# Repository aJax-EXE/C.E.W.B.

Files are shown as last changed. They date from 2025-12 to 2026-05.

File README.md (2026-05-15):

# C.E.W.B.: The Open Source Teaching Platform for Control Systems
**ECEN4620/MCEN4085: Senior Design Project - University of Colorado Boulder**  
**Sponsors:** Talles Santos  
&emsp;&emsp;&emsp;&emsp;&emsp; Nathan McNeil  
**Students:** [Alyssa Jackson](https://github.com/aJax-EXE) (Electrical and Computer Engineering)  
&emsp;&emsp;&emsp;&emsp;&emsp;Eric Pollert (Mechanical Engineering)  
&emsp;&emsp;&emsp;&emsp;&emsp;[Isaiah Knox](https://github.com/iknox001) (Mechanical Engineering)  

---

## Table of Contents
1. [Introduction](#introduction)
2. [Project Overview](#project-overview)
3. [System Specifications](#system-specifications)
4. [Repository Structure](#repository-structure)
5. [Hardware](#hardware)
   - [Circuit Design](#circuit-design)
   - [Data Transmission](#data-transmission)
   - [Accessory Storage](#accessory-storage)
   - [Device Deck](#device-deck)
   - [Motor Housing](#motor-housing)
   - [Electrical Compartment](#electrical-compartment)
   - [Attachments](#attachments)
6. [Software](#software)
   - [Dependencies](#dependencies)
   - [Arduino Code](#arduino-code)
   - [MATLAB/Simulink Interface](#matlabsimulink-interface)
   - [Custom Libraries](#custom-libraries)
7. [Getting Started](#getting-started)
   - [Hardware Setup](#hardware-setup)
   - [Software Setup](#software-setup)
   - [Running Your First Experiment](#running-your-first-experiment)
8. [Lab Experiments](#lab-experiments)
   - [Angular Position Control (Inertia Disc)](#angular-position-control-inertia-disc)
   - [Inverted Pendulum Balancing](#inverted-pendulum-balancing)
9. [Results](#results)
10. [Known Limitations](#known-limitations)
11. [Next Steps](#next-steps)
    - [List of Issues](#list-of-issues)
    - [After CEWB Functionality is Reached](#after-cewb-functionality-is-reached)
12. [Contributing](#contributing)
13. [License](#license)

---

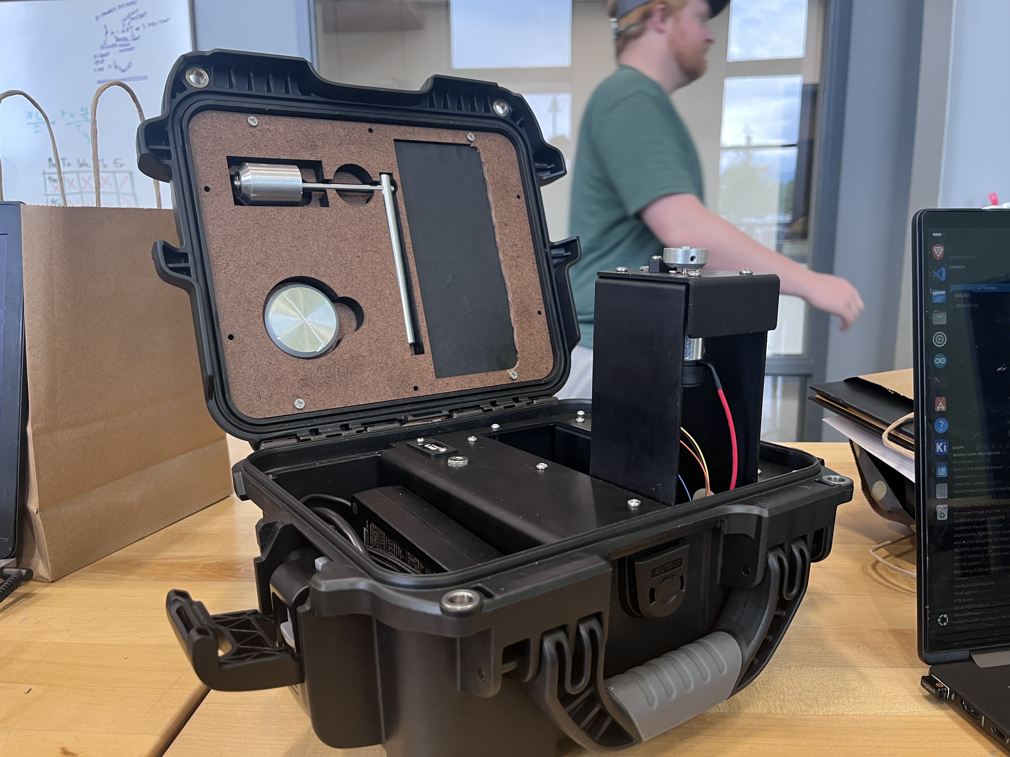
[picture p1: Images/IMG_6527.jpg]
The CEWB
  
*The CEWB, fully built*  
&emsp;

---

## Introduction

C.E.W.B. (name pending; referred to as 'CEWB' throughout this README) is a low-cost, open-source electromechanical teaching platform designed for teaching and applying control systems concepts in a real-world environment. It was developed as a direct functional replacement for the Quanser Qube-Servo 2, a $5,000 proprietary device that is now outdated and requires an older version of MATLAB to operate.

The device supports the same core laboratory experiments as the Qube-Servo 2, including angular position control with an inertia disc and inverted pendulum balancing. It is designed to be self-contained, portable, and fully compatible with MATLAB and Simulink.

All design files, code, and documentation are publicly available in this repository so that the device can be reproduced by any institution without reliance on proprietary hardware or software.

---

## Project Overview

This project set out to design a low-cost, open-source replacement for the Quanser Qube-Servo 2, a $5,000 device used in control systems classes. The target was a fully functional prototype delivered by May 2026 at under $1,000 per unit, capable of supporting the same lab experiments — including angular position control with an inertia disc and inverted pendulum balancing — while being self-contained, portable, and compatible with MATLAB/Simulink.

The design integrates all components into a Nanuk 905 protective case with built-in storage for attachments, cables, and the power supply. The system uses an Arduino microcontroller, a motor driver, and a custom PCB, with two interchangeable magnetic attachments — an inertia disc and a pendulum — mirroring the Qube-Servo 2's functionality. The projected per-unit production cost of $763.68 comes in well under the $1,000 target.

The device met most implementation requirements. Data transmission, MATLAB/Simulink compatibility, third-party manufacturability, self-contained storage, and transport protection all passed evaluation. Open-source documentation, including CAD files, a bill of materials, and assembly instructions, has been prepared and made publicly available.

However, the device did not fully replicate the closed-loop control performance of the Qube-Servo 2. The Arduino's data transmission rate is approximately an order of magnitude slower than the proprietary controller used in the Qube-Servo 2, causing significant control loop delays and excessive overshoot during inertia disc testing. As a result, the pendulum balancing test was not attempted.

The primary recommended next step is to replace the Arduino with a faster microcontroller, retest the system using the same control experiments, and proceed to a small production run once performance requirements are confirmed to be met.

---

## System Specifications

The following table lists the key performance parameters of the C.E.W.B. system alongside the Qube-Servo 2 equivalents for reference.

| Parameter | C.E.W.B. | Qube-Servo 2 |
|---|---|---|
| Motor | Maxon DC-max 26 S Ø26 mm | Maxon (discontinued) |
| Nominal input voltage | 24 V | 18 V |
| Nominal torque | 22.0 mN-m | 22.0 mN-m |
| Nominal speed | 3050 RPM | 3050 RPM |
| Encoder line count | 512 lines/rev | 512 lines/rev |
| Encoder resolution (quadrature) | 2048 counts/rev | 2048 counts/rev |
| Encoder resolution (deg) | 0.176 deg/count | 0.176 deg/count |
| Encoder resolution (rad) | 0.00307 rad/count | 0.00307 rad/count |
| Motor controller | Adafruit DRV8871 | PWM amplifier |
| Microcontroller | Arduino Uno R3 | Proprietary |
| Data transmission rate | ~50 Hz (USB serial) | ~500 Hz (proprietary) |
| Output voltage range | ±24 V | ±10 V (recommended) |
| Per-unit cost (production) | $763.68 | $5,000.00 |

---

## Repository Structure

```
C.E.W.B./
├── Datasheets/
│   ├── Electrical/                                # Datasheets for all electrical components
│   └── Hardware/                                  # Datasheets for hardware components
├── Documentation/                                # Documentation from the Senior Projects Class
├── Hardware/
│   ├── 3DModels/
│   │   ├── CurrentVersion/                       # Final production CAD files (SolidWorks)
│   │   │   ├── Device Components/                # All structural device parts
│   │   │   │   ├── Full Assembly.SLDASM
│   │   │   │   ├── Motor Arm.SLDASM
│   │   │   │   ├── Housing.SLDPRT
│   │   │   │   ├── Motor Plate.SLDPRT
│   │   │   │   ├── Motor Leg.SLDPRT
│   │   │   │   ├── Plate bend inlet.SLDPRT
│   │   │   │   ├── Inertia Disc.SLDPRT
│   │   │   │   ├── Attachment Interface.SLDPRT
│   │   │   │   ├── Pendulum Assembly.SLDASM
│   │   │   │   ├── Pendulum mount.SLDPRT
│   │   │   │   ├── Pendulum shaft.SLDPRT
│   │   │   │   ├── Pendulum Arm.SLDPRT
│   │   │   │   ├── Pendulum Stop.SLDPRT
│   │   │   │   ├── PCB.SLDPRT
│   │   │   │   ├── PCB Mounting Plate.SLDPRT
│   │   │   │   └── [purchased hardware SLDPRTs]
│   │   │   └── Storage Compartment Components/   # Lid storage assembly parts
│   │   │       ├── Foam_Panel.SLDPRT
│   │   │       ├── Front Panel.SLDPRT
│   │   │       └── Rear Lid Panel.SLDPRT
│   │   └── PastVersions/                         # Design iteration history
│   └── PCBModels/
│       ├── ArduinoShieldDesign/                  # KiCad PCB design files
│       │   ├── ForwardDesign/                    # Current production PCB
│       │   ├── ReverseDesign/                    # Earlier PCB iteration
│       │   ├── OldTestBoard/                     # First test board
│       │   └── PotentialFix/                     # Proposed PCB fix iteration
│       ├── GerberFiles/
│       │   ├── ForwardFiles/                     # Gerber files for production PCB
│           └── ReverseFiles/                     # Gerber files for reverse design
├── Images/                                       # Images used in this README and in the documentation
├── Software/
│   ├── Libraries/                                # Arduino libraries — install these manually
│   │   ├── CombiningEncoderCounts/               # CEWBEncoder source
│   │   │   ├── CEWBEncoder.cpp
│   │   │   └── CEWBEncoder.h
│   │   └── OtherFunctions/                       # CEWBFunctions source
│   │       ├── CEWBFunctions.cpp
│   │       └── CEWBFunctions.h
│   ├── ExamplesAndTests/
│   │   ├── ArduinoTests/                         # Standalone Arduino diagnostic sketches
│   │   │   ├── CalcToAnalogVal/                  # PWM value calculator
│   │   │   ├── CommunicationConstantlySendingData/  # Serial format test
│   │   │   ├── EncoderQuadTest/                  # Encoder wiring verification
│   │   │   ├── InterruptEncoderTest/             # Interrupt-based encoder test
│   │   │   └── MotorRampSpeedTest/               # Motor driver verification
│   │   ├── ProofOfConcept/                       # Early proof-of-concept scripts
│   │   └── SimulinkTests/                        # Simulink integration test models
│   │       ├── BasicSimulinkCommunication/       # Initial serial block example
│   │       ├── BypassSerialBlockSimulinkConnectionTest/
│   │       ├── CompleteSimulinkRunTest/
│   │       │   ├── BasicRunning/                 # Open-loop voltage test model
│   │       │   └── WorkingModel/                 # ⭐ Main working model
│   │       │       ├── ArduinoSerial.m           # MATLAB System block
│   │       │       ├── WorkingModel.ino          # Arduino sketch
│   │       │       └── PIDController.slx         # Simulink model
│   │       ├── SimulinkFormattingTest/
│   │       └── SimulinkReadEncoder/              # Encoder-only read test
│   ├── SendingBytesTest/                         # Binary byte transmission experiment
│   ├── SimulinkReadWriteSerialPort/              # Early serial block experiments
│   ├── SpinMotorWithSimulinkTest/                # Motor spin test
│   └── UpgradedMotorWSimulinkTest/               # Updated motor test
├── .gitignore
└── README.md
```
 
> ⭐ **For most users, the only files needed are in `Software/ExamplesAndTests/SimulinkTests/CompleteSimulinkRunTest/WorkingModel/`** — the Arduino sketch, MATLAB System block, and Simulink model are all there.
---

## Hardware

&emsp;
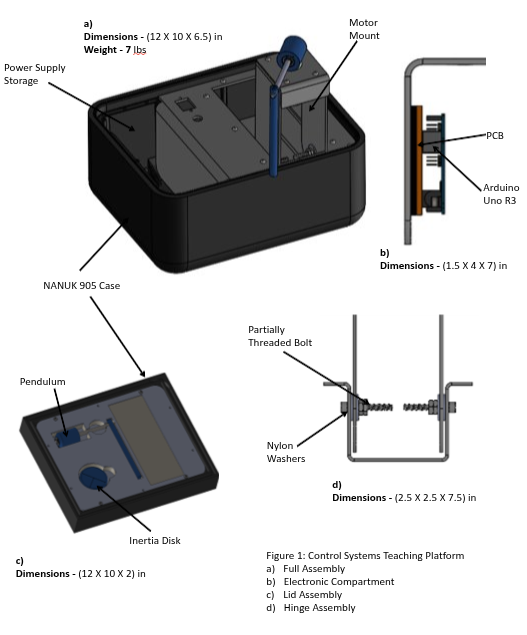
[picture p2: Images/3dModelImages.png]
3D Models of the CEWB
  
*3D models of the CEWB and its parts*  
&emsp;

### Circuit Design

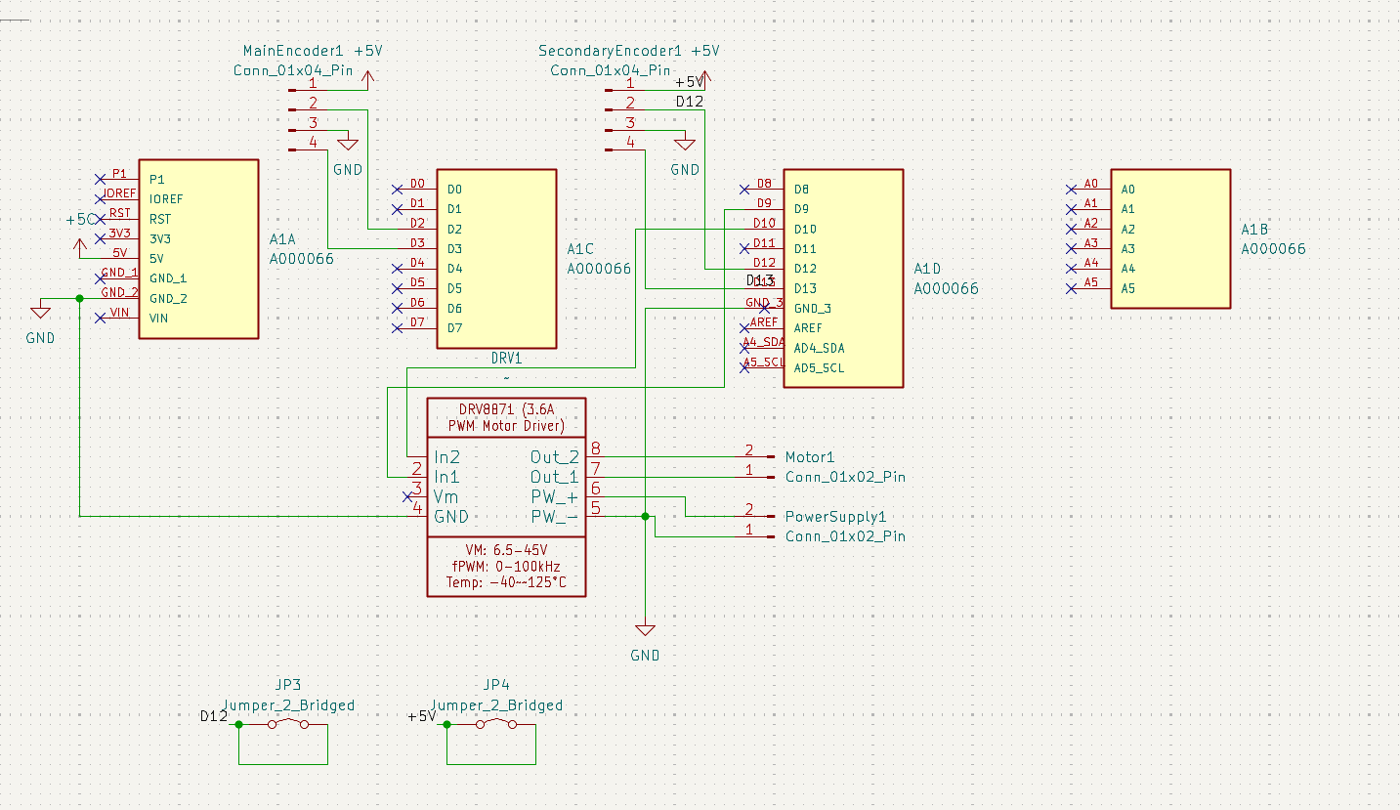
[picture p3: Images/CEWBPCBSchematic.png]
The CEWB Schematics
  
*The CEWB electrical schematic*  
&emsp;

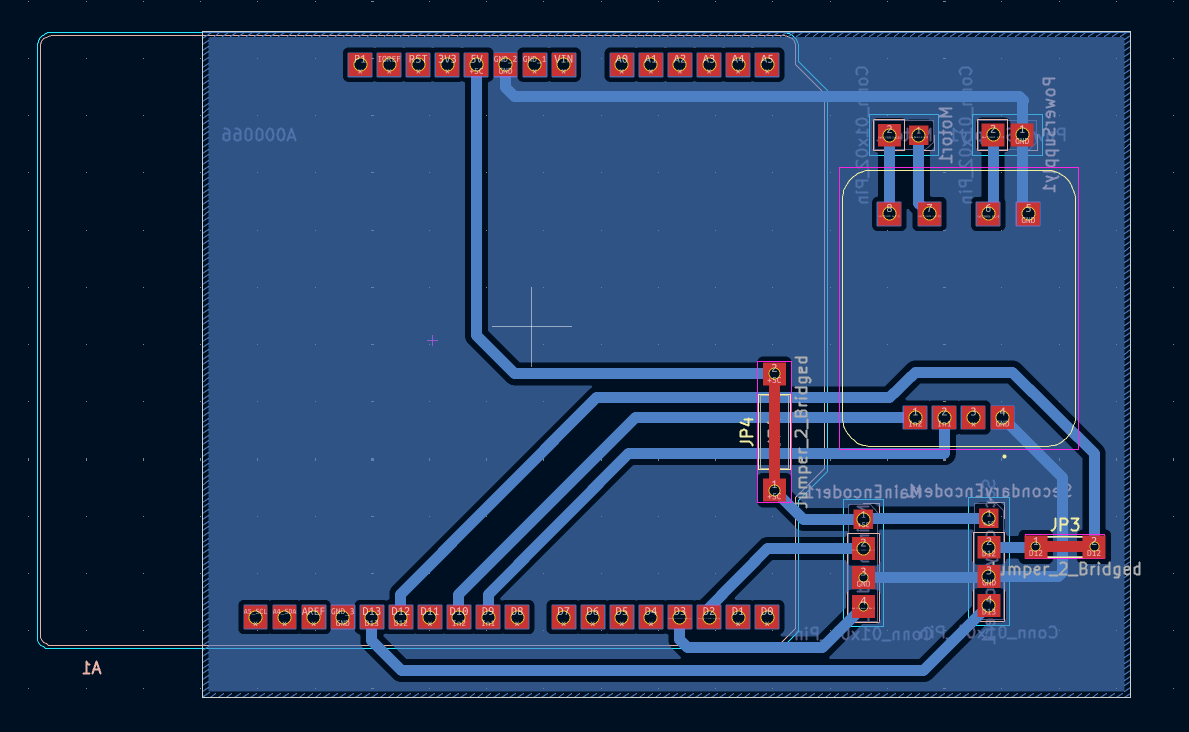
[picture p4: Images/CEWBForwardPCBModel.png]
The CEWB PCB Model
  
*The CEWB PCB model*  
&emsp;

The electrical system is built around an Arduino Uno R3 microcontroller and an Adafruit DRV8871 motor driver, both connected through a custom PCB. The PCB acts as a junction point between the motor, encoders, and microcontroller, consolidating all wiring and reducing the risk of loose connections. A 24V Mean Well GST90A24-P1M power supply provides power to the system via a front-panel power port. A front-panel USB-B port connects the Arduino to the user's laptop for data transmission.

The PCB is insulated from the aluminum mounting panel using an acrylic backing plate to prevent electrical interference.

### Data Transmission

Communication between the Arduino and MATLAB/Simulink is handled over USB serial at 115200 baud using a custom request/response packet protocol. Simulink sends a scaled integer voltage command, and the Arduino responds with the current encoder count and applied voltage. The full protocol is described in the [Arduino Code](#arduino-code) section of the Software documentation.

### Accessory Storage

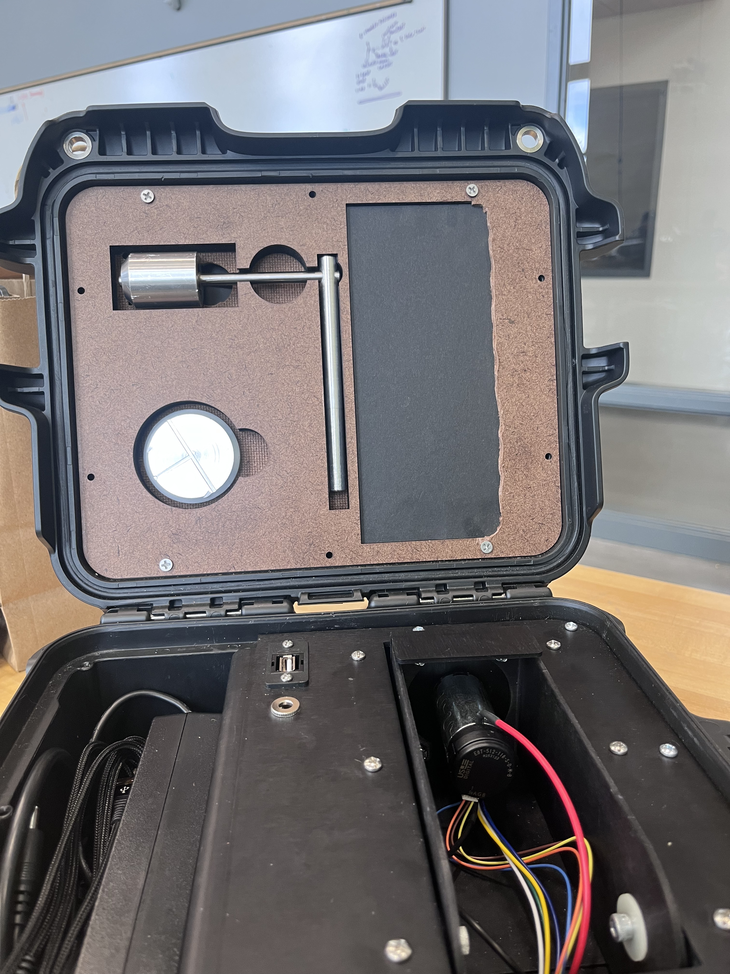
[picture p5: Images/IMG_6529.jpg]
The Storage Lid
  
*The storage lid that houses the CEWB attachments*  
&emsp;

The accessory storage compartment is made up of two pieces of hardboard and one piece of foam with cutouts for the accessories to fit into. The rear panel of hardboard has magnets glued into it, which allow the attachments to be secured in their respective locations during storage. Hardboard was selected for the front and rear panels as it is a light, cheap, and sturdy material. Foam was chosen for the middle panel as it is low-density and fills the space between the boards without significantly increasing weight. The three panels are glued together with super glue and are fixed into the top of the Nanuk 905 case using thread-forming screws.

### Device Deck

The main part of the deck of the device is a bent piece of aluminum sheet metal which is screwed into the Nanuk 905 case using thread-forming screws and serves as a mounting plate for the rest of the components. This part is bent to create a compartment for storing the power supply and the data transmission cable. The top surface of this panel has two ports: a USB port where the data transmission cable is plugged in, and a power port where the device is connected to the power supply. The ports were added to clean up the visual appearance of the device and remove the need for cables to be plugged directly into the electrical compartment. On the right side of the panel there is a cavity with a U-shaped bent piece of aluminum sheet metal mounted to the bottom of the panel, which serves both as a mounting location for the motor housing and as a barrier between the user and the internal components. The cavity allows the motor housing to fold into the device when stored. The trough contains a hole to allow wires to pass through between the motor housing and the electrical compartment. This hole is lined with a silicone grommet which protects the wires from fraying when the motor housing is moved between its storage and operating positions.

### Motor Housing

The motor housing consists of three main structural components, all made from aluminum sheet metal. The two motor housing legs give the housing the height required for the pendulum attachment and serve as the mounting location for the hinge, which allows the housing to pivot between its operational and storage positions. The hinge consists of a partially threaded socket head screw, nuts, and nylon washers. The partially threaded screw was chosen to provide a smooth surface for the hinge to rotate on. The nylon washers secure the housing in place during operation while still allowing rotation under sufficient force to slightly deform the nylon. The two washers at the end are jammed together to secure the hinge at a calibrated tightness, ensuring the hinge can be rotated but remains secured during operation.

The third structural component is the motor mounting plate, which features a bend that serves as a handle when switching the device between positions. This plate is attached at the top of the two motor legs using bolts and locknuts, and has the motor mounted to its underside using machine screws secured directly into threaded holes in the top of the motor. The motor is from Maxon and was chosen to replicate the motor of the Qube-Servo 2 as closely as possible given that the original motor is no longer available. An optical encoder is mounted to the rear axle of the motor using double-sided adhesive, which allows the encoder to be secured firmly without screws, as there are no mounting locations on the rear of the motor. The attachment interface is a small machined aluminum disc mounted to the end of the top motor shaft using a set screw. This component has magnets that allow the attachments to be fixed to the motor shaft during use. The motor plate also has a small 3D-printed elbow-shaped component mounted near the motor, which serves as a stop to prevent the pendulum from over-rotating and damaging its wiring. The mounting plate also has a 3.5 mm jack port for connecting the encoder from the pendulum attachment during use.

### Electrical Compartment

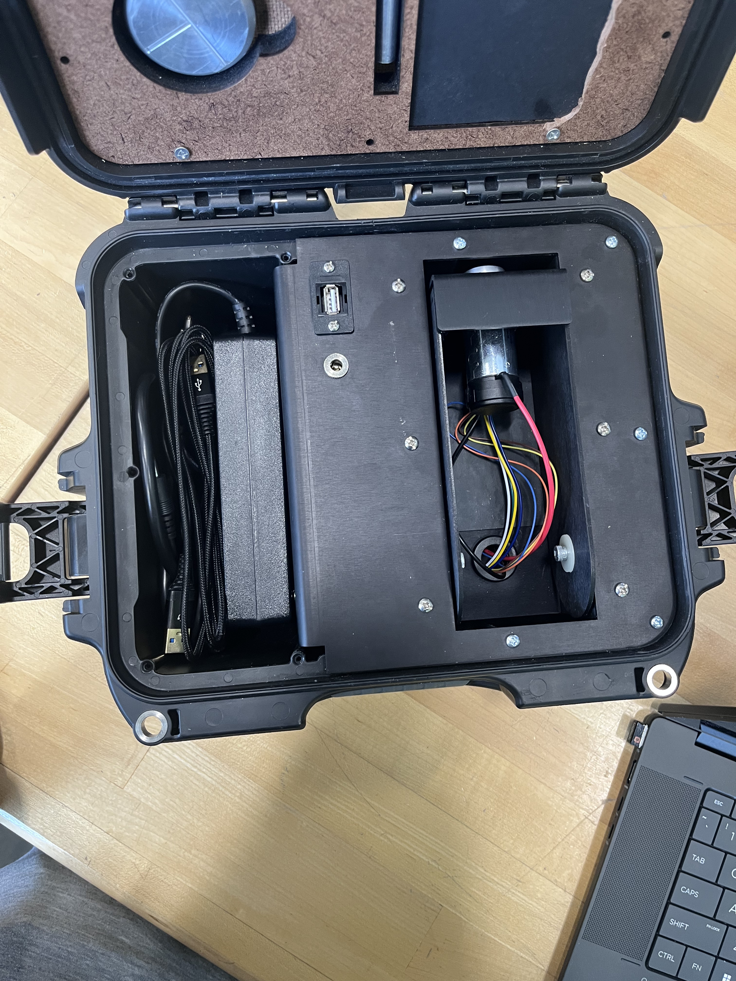
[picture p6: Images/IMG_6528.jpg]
The CEWB electrical compartment
  
*The CEWB electrical compartment*  
&emsp;

The electrical compartment is located between the bend in the top panel of the device deck and the trough. The electrical components — including the motor driver, Arduino, and PCB — are mounted to the backside of the panel using nuts and bolts, with a piece of acrylic sized to match the PCB placed behind it to insulate the exposed circuitry from the aluminum panel and prevent electrical interference.

### Attachments

The two attachments are the inertia disc and the pendulum. The inertia disc is a machined aluminum disc which adds rotational inertia to the motor shaft for use in position control experiments. The disc has lines engraved into its top surface which allow the user to visually track the motor's position and verify control system behavior. The disc has four magnets on the back which allow it to be secured to the attachment interface during use and to the attachment storage compartment when stored.

The pendulum consists of three machined components. The pendulum cylinder is machined from aluminum and is the mounting location for the pendulum assembly. It has magnets on one side for mounting to the attachment interface and storage compartment, and two bearings press-fit into its internal bore which allow the pendulum axle to rotate freely. The pendulum axle is made from steel and is inserted through the two bearings and secured using two retaining rings that fit into grooves in the axle positioned to press against the bearings. An optical encoder is attached to the pendulum cylinder using machine screws and tracks the angular position of the axle during pendulum experiments. The encoder connects via a 3.5 mm cable to a jack on the motor mounting plate, allowing encoder data to be transmitted to the electrical compartment. The pendulum arm is mounted on the far end of the axle using a set screw and acts as a counterweight to create the tipping moment that the control system must compensate for in the inverted pendulum experiment.

---

## Software

### Dependencies

**Arduino IDE (1.8.x recommended)**
- CEWBEncoder (included in `Software/MATLAB/Libraries/CEWBEncoder/`)
- CEWBFunctions (included in `Software/MATLAB/Libraries/CEWBFunctions/`)

**MATLAB/Simulink**
- MATLAB R2024b or later
- Simulink
- No additional toolboxes required — serial communication is handled via a custom `matlab.System` object

### Arduino Code

The main Arduino sketch (`WorkingModel.ino`) implements a simple request/response serial protocol. Simulink sends a voltage command, the Arduino executes it on the motor, and responds with the current encoder count and applied voltage.

**Packet format:**

| Direction | Format | Example |
|---|---|---|
| Simulink → Arduino | `#sXXXXXX\n` | `#+037500\n` (3.75V × 10000) |
| Arduino → Simulink | `#sXXXXXX,sXXXXXX\n` | `#+000512,+037500\n` |

Voltage is transmitted as a scaled integer (real volts × 10000) to preserve 4 decimal places without transmitting a decimal point. Conversion is handled by `makeVoltage()` in CEWBFunctions.

The Arduino also implements a **500ms watchdog** — if no packet is received within 500ms (e.g. if Simulink is stopped or the USB cable is disconnected), the motor is cut automatically.

### MATLAB/Simulink Interface

Communication between Simulink and the Arduino is handled by `ArduinoSerial.m`, a `matlab.System` subclass that runs a 200Hz background timer independently of the Simulink step rate. This decouples serial timing from Simulink's solver, allowing smoother encoder data with less blocking.

**Block interface:**

| Port | Direction | Description |
|---|---|---|
| `v_in` | Input | Voltage command (−6 to +6 V) |
| `enc_out` | Output | Raw encoder count |
| `v_out` | Output | Voltage currently applied (for scope) |

**Configurable block parameters (set by double-clicking the block):**

| Parameter | Default | Description |
|---|---|---|
| `COMPort` | `/dev/ttyACM0` | Serial port (Linux) or `COM3` (Windows) |
| `BaudRate` | `115200` | Serial baud rate |
| `TimerPeriod` | `0.005` | Background timer period in seconds (0.005 = 200Hz) |

To convert `enc_out` to angle, wire it through a Gain block set to `(2*pi)/2048` for radians or `360/2048` for degrees.

### Custom Libraries

**CEWBEncoder**  
Interrupt-driven quadrature encoder library supporting ENC1X, ENC2X, and ENC4X decoding modes using Arduino pin change interrupts (PCINT). Supports up to 8 encoders simultaneously.

Key functions:
```cpp
CEWBEncoder enc(pinA, pinB, ENC4X);  // constructor
enc.begin();                          // enable interrupts
enc.getCount();                       // returns long count
enc.getDirection();                   // returns -1, 0, or 1
enc.resetCount();                     // resets count to zero
```

**CEWBFunctions**  
Utility functions for motor voltage conversion.

Key functions:
```cpp
voltToPWM(float voltage);   // converts voltage magnitude to PWM (0-255)
PWMToVolt(uint8_t PWM);     // converts PWM back to voltage
makeVoltage(long value);    // descales integer (value / 10000.0) to float volts
```

Note: `voltToPWM` maps voltage against a 24V maximum (`maxVolt = 24`). Passing values above 24V returns 255. Always pass `fabsf(voltage)` — direction is handled separately by `spinMotor`.

---

## Getting Started

### Hardware Setup

1. Connect the USB-B cable from the device's front panel USB port to your laptop.
2. Connect the power cable to the device's front panel power port and plug it into the wall.
3. Raise the motor housing to its upright operating position.
4. Attach the desired attachment (inertia disc or pendulum) to the motor interface magnetically.
5. If using the pendulum attachment, plug the 3.5 mm encoder cable into the jack on the motor plate.

> ⚠️ **Before use, ensure the motor housing is in the upright position and that power and computer cables — along with any other objects — are clear of the motor shaft.**

### Software Setup

**Arduino:**
1. Install Arduino IDE 1.8.x.
2. Copy `CEWBEncoder` and `CEWBFunctions` folders from `Software/MATLAB/Libraries/` into your Arduino libraries directory:
   - Linux (Snap): `~/snap/arduino/85/Arduino/libraries/`
   - Linux (AppImage/standard): `~/Arduino/libraries/`
   - Windows: `Documents/Arduino/libraries/`
3. Open `Software/Arduino/WorkingModel/WorkingModel.ino` in Arduino IDE.
4. Select **Tools → Board → Arduino Uno** and the correct port under **Tools → Port**.
5. Upload the sketch.

**MATLAB/Simulink:**
1. Place `ArduinoSerial.m` in the same folder as your Simulink `.slx` model file — Simulink looks for it by name in the current working directory.
2. Open your Simulink model.
3. Add a **MATLAB System** block (Simulink → User-Defined Functions → MATLAB System).
4. Double-click the block and select `ArduinoSerial` from the dropdown.

> ⚠️ **If `ArduinoSerial` does not appear in the dropdown, the `.m` file is not in the same folder as your Simulink model. Move it and try again.**

5. Set `COMPort` to match your Arduino's port (check Arduino IDE → Tools → Port).
6. Set the Simulink solver to **Fixed-step**, step size `0.02` (Ctrl+E → Solver).
7. Press **Play** — the block handles serial port opening, the background timer, and cleanup automatically.

### Running Your First Experiment

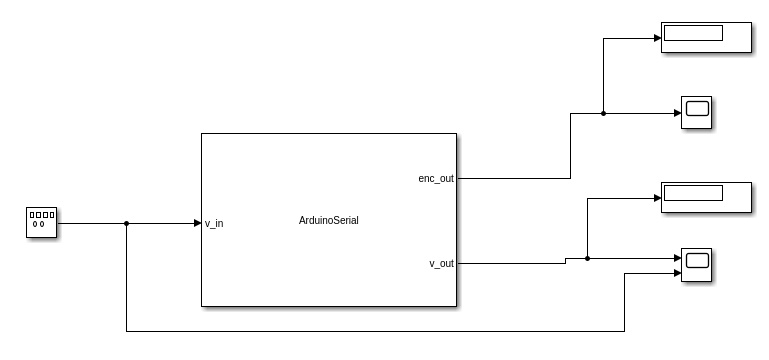
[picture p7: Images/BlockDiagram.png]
Block Diagram of voltage input and encoder output
  
*The block diagram of the first example experiment*  
&emsp;

A simple open-loop voltage test:
1. Add a **Signal Generator** block (square wave, amplitude 3, frequency 0.5 Hz).
2. Wire it to `v_in` on the ArduinoSerial block.
3. Add a **Gain** block after `enc_out` with value `360/2048` to convert counts to degrees.
4. Connect both the Gain output and `v_out` to a **Scope** block.
5. Press **Play**. The motor should respond to the square wave and the scope should display the angular position and applied voltage.

---

## Lab Experiments

### Angular Position Control (Inertia Disc)

**Objective:** Command the inertia disc to move between angular positions (e.g. +1 rad and −1 rad) while minimizing overshoot using a PID controller.

**Simulink wiring:**
```
Constant (setpoint, rad) ──► Sum(+−) ──► PID ──► Saturation(±6V) ──► v_in ──► ArduinoSerial
                                ▲                                                      │
                                └──────────── Gain(2π/2048) ◄──── enc_out ────────────┘
```

**Recommended starting PID gains:**

| Gain | Starting Value |
|---|---|
| Kp | 0.1 |
| Ki | 0.0 |
| Kd | 0.1 (use filtered derivative: `10s/(s+10)`) |

> **Important:** Do not use Simulink's built-in `Derivative` block — it has infinite gain at high frequencies and will amplify serial timing noise, causing unstable motor behavior. Use a `Transfer Fcn` block with numerator `[10 0]` and denominator `[1 10]` instead.

**Note:** Due to the Arduino's ~20ms serial round-trip latency, aggressive PID gains will cause instability. Start with a low Kp and no derivative term, then increase gradually.

### Inverted Pendulum Balancing

> **Status: Not yet validated.** The inverted pendulum experiment requires faster closed-loop performance than the current Arduino-based system can reliably provide. This experiment is planned for a future hardware revision using a faster microcontroller. See [Next Steps](#next-steps).

---

## Results

The device met the following design requirements:

| Requirement | Target | Result |
|---|---|---|
| Accurate data transmission | Pass | ✅ Pass |
| MATLAB/Simulink compatibility | Pass | ✅ Pass |
| Cost target | < $1,000 | ✅ $763.68 |
| Self-contained storage | Pass | ✅ Pass |
| Transport protection | Pass | ✅ Pass (Nanuk 905, ASTM D-4169 DC-18 certified) |
| Third-party manufacturability | Pass | ✅ Pass |
| Software updatability | Pass | ✅ Pass (on supported MATLAB versions) |
| Qube function replication | Pass | ❌ Partial — inertia disc overshoot; pendulum not attempted |
| Motor and encoder performance | Comparable | ❌ Not met under closed-loop conditions |

---

## Known Limitations
**Serial latency (~20ms round-trip)**  
The Arduino Uno communicates over USB serial at approximately 50Hz, compared to the Qube-Servo 2's ~500Hz proprietary interface. This introduces significant control loop delay, causing excessive overshoot at higher PID gains. The background timer in `ArduinoSerial.m` partially mitigates this by running at 200Hz independently of Simulink, but the underlying serial round-trip remains the bottleneck.

**Encoder noise at high motor speeds**  
At high voltages, motor vibration can introduce noise on the encoder signal lines, causing occasional miscounts. Adding 10–100nF ceramic capacitors between each encoder signal pin and GND reduces this significantly.

**`voltToPWM` maps against 24V maximum**  
The `voltToPWM` function in CEWBFunctions maps input voltage against a 24V maximum. Voltages in the recommended ±6V operating range use only 25% of the available PWM range. If finer motor resolution is needed, change `maxVolt` in `CEWBFunctions.cpp` to match your intended operating voltage range.

---

## Next Steps

### List of Issues

In order to address the fundamental limitations of the CEWB and improve it in future iterations, the following items should be investigated:

- **Research faster microcontrollers**  
  The Arduino Uno R3 is not powerful enough to spin the motor, count the encoder position, and transmit/receive data to and from Simulink accurately in real time. To improve throughput and reduce computational bottlenecks, consider:
  - Using a single faster microcontroller (Raspberry Pi Pico, STM32, Teensy 4.x, etc.)
  - Using two or more microcontrollers with divided responsibilities — e.g. one handling motor control and encoder counting while another manages data transmission

- **Switch data transmission from strings to bytes**  
  The current string-based packet format is human-readable and useful for debugging, but binary byte transmission is significantly faster. The string format should be retained as a diagnostic/test option, but the production firmware should use binary packets.

- **Research higher-rate data transmission methods**  
  The Arduino Uno communicates at approximately 50Hz while the Qube-Servo 2 operates at ~500Hz. Investigate how the Qube-Servo 2 achieves this rate and identify equivalent approaches for the CEWB.

- **Look into wireless encoders for the inverted pendulum**  
  With the current setup, the pendulum attachment cannot rotate continuously 360° because of the wire connecting to the audio jack port on the motor plate. While this is sufficient for balancing at 180°, a wireless encoder connection would eliminate the rotation constraint and enable more complex experiments.

- **Add a strap to secure the inverted pendulum attachment in storage**  
  Currently, the pendulum shaft falls out of its storage cutout and props the lid open, preventing it from closing. A simple retaining strap would resolve this without requiring significant redesign.

- **Develop additional inertia disc variants**  
  Additional discs of different masses and radii would provide a wider range of system dynamics, enriching the experiments that can be demonstrated and taught.

- **Combine the `CEWBEncoder` and `CEWBFunctions` libraries**  
  Consolidating both libraries into a single library would not improve performance but would simplify installation and make the codebase easier for users to navigate.

- **Refine 3D models**  
  Minor dimensional discrepancies have been observed in received parts. While all parts are functional, tighter tolerances and updated models would reduce the need for post-receipt modification.

- **Document fabrication vendors and order specifications**  
  For the project to scale to wider adoption, the specific vendors used and the exact order specifications (dimensions, material, finish, etc.) for each custom part should be documented in the repository.

- **Investigate current surge protection**  
  If the motor stalls, current can spike and potentially damage other electrical components. Additional protection circuitry beyond the motor driver's built-in limiting should be explored.

- **Finalize the C.E.W.B. name**  
  The name was conceived to copy the Qube's spelling but does not currently stand for anything. A meaningful acronym or a new name entirely should be decided upon before wider release.

- **Research ways to make the motor run quieter**  
    The motor constantly emits a low and piercing buzz that can cause headaches. Look into making that stop and run quiet like the Qube does.

### After CEWB Functionality is Reached

Once the CEWB achieves reliable closed-loop performance, the following steps are planned:
1. Retest angular position control with the inertia disc using the same PID experiments
2. Attempt and validate inverted pendulum balancing
3. Assemble a small production run for deployment in the control systems course
4. Provide a prototype unit to the course instructor for curriculum integration

---

## Contributing

This project is open-source and contributions are welcome. To contribute:

1. Fork the repository
2. Create a feature branch (`git checkout -b feature/your-feature`)
3. Commit your changes (`git commit -m 'Add your feature'`)
4. Push to the branch (`git push origin feature/your-feature`)
5. Open a pull request

For questions or technical support, contact:
- **Dr. Talles Santos** (project sponsor): Talles.Santos@colorado.edu
- **Dr. Nathan McNeil** (project sponsor): Nathan.Mcneil@colorado.edu
- **Alyssa Jackson** (project member): alyssajackson436@gmail.com
- **US Digital** (encoders): support@usdigital.com | 800-736-0194
- **Maxon Motors**: info.us@maxongroup.com | (508) 677-0520

---

## License

This project is open-source. All CAD files, code, and documentation are made publicly available for reproduction and modification. See the repository for license details.

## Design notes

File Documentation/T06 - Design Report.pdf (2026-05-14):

Open-Source Teaching Platform for Control Systems: Design Report

# Open-Source Teaching Platform for Control Systems:

# Design Report

# Isaiah Knox, Alyssa Jackson, and Eric Pollert

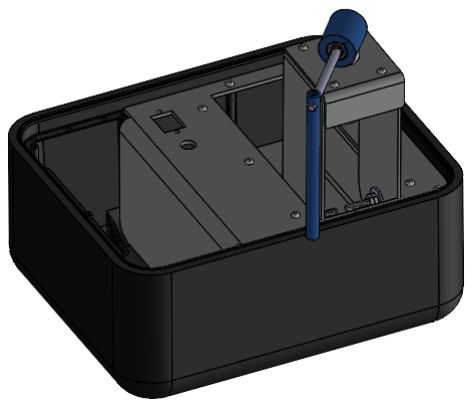
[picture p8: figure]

## Contents

### 1 Executive Summary | 3

### 2 Problem Definition | 3

2.1 | Problem Scope | 3
2.2 | Technical Review | 3
2.3 | Design Requirements | 3

### 3 Design Description | 4

3.1 | Overview | 4
3.2 | Detailed Description | 4
3.3 | Use | 6

### 4 Design Evaluation | 7

4.1 | Overview | 7
4.2 | Evaluation of Design Criteria | 7

4.2.1 Qube Function Replication | 7 4.2.2 Motor and Encoder Performance | 8 4.2.3 Accurate Data Transmission | 8 4.2.4 Cost Target | 9 4.2.5 Self-Contained Storage | 9 4.2.6 Transport Protection | 10 4.2.7 MATLAB/Simulink Compatibility | 10 4.2.8 Software Updatability | 10 4.2.9 Third-Party Manufacturability | 11 4.2.10 Device Evaluation Summary | 11
4.3 | Conclusions | 12
4.4 | Next Steps | 12

### 5 Appendix | 13

5.1 Quanser Qube-Servo 2 Specifications Table | 13

## 1 Executive Summary

This project set out to design a low-cost, open-source replacement for the Quanser Qube-Servo 2, a $5,000 device used in control systems classes. The target was a fully functional prototype delivered by May 2026 at under $1,000 per unit, capable of supporting the same lab experiments, including angular position control with an inertia disc and inverted pendulum balancing, while being self-contained, portable, and compatible with MATLAB/Simulink.

The design integrates all components into a Nanuk 905 protective case with built-in storage for attachments, cables, and the power supply. The system uses an Arduino microcontroller, a motor driver, and a custom PCB, with two interchangeable magnetic attachments, an inertia disc and a pendulum, mirroring the Qube-Servo 2's functionality. The projected per-unit production cost of $763.68 comes in well under the $1,000 target.

The device met most implementation requirements. Data transmission, MATLAB/Simulink compatibility, third-party manufacturability, self-contained storage, and transport protection all passed evaluation. Open-source documentation, including CAD files, a bill of materials, and assembly instructions, has been prepared and made publicly available.

However, the device did not fully replicate the closed-loop control performance of the Qube-Servo 2. Arduino’s data transmission rate is approximately an order of magnitude slower than the proprietary controller used in the Qube-Servo 2, causing significant control loop delays and excessive overshoot during inertia disc testing. As a result, the pendulum balancing test was not attempted.

The primary recommended next step is to replace the Arduino with a faster microcontroller, retest the system using the same control experiments, and proceed to a small production run once performance requirements are confirmed to be met.

## 2 Problem Definition

### 2.1 Problem Scope

The purpose of this project is to design a device for students taking control systems to gain hands-on experience with the implementation of control systems, such as PID circuits, to run simple tasks on a real mechanical device. This device will replace the Quanser Qube-Servo 2, which is currently utilized by the instructor to accomplish these goals. The device must function similarly to the Qube-Servo 2, and mechanical components such as the DC motor must maintain similar specifications to ensure the device can be used to complete the projects that are completed as part of the control systems class. The team was tasked with developing a working prototype of this device, testing this device to ensure the performance matches the expectations of the project sponsors, and completing the preparation work that will be necessary for the sponsors to order all the components of the device from third-party manufacturing companies. This device must be open source and have the ability to be updated so that it will not go obsolete as the software it depends on goes obsolete. A fully functioning final prototype of this device is required to be delivered by May 1, 2026, and all necessary information necessary to reproduce the device, such as CAD files, a bill of materials, assembly steps, and clearly documented code, must be delivered to the sponsors by May 11, 2026. The design team was not responsible for a full production run of the device or acquiring certifications for the device. The design of this project is focused on replicating the functionality of the Qube-Servo 2 and only making changes necessary to meet the design requirements, not adding additional attachments to the device or expanding the number of projects that can be completed by the device.

### 2.2 Technical Review

As the purpose of the project is to design a device to replace the Qube-Servo 2, most of the reviewed material relates directly to that system. The documentation and user instructions for the Qube-Servo 2 were used to identify key specifications for major components such as the motor and encoders. This includes values like the motor torque constant and rotor inertia, as well as encoder line count and resolution. These values, along with other relevant parameters, are listed in a specifications table in the Appendix and were used as a baseline for comparison. During the review of the device, it was found that the Qube-Servo 2 uses a proprietary microcontroller. Because of this, the original control code could not be accessed or reviewed, which limits direct understanding of how the system operates at the software level. The device also uses a separate motor controller to send commands from the microcontroller to the motor, along with an additional circuit board to reduce internal wiring and manage connections between components. When the pendulum attachment was disassembled, it was found to consist of three custom-machined parts, two bearings, an optical encoder, and standard fasteners. The inertia disk attachment follows a similar structure. Both attachments connect to the motor using magnets, which allows them to be attached and removed without tools. The overall system is made up of several separate components. These include the main cube, which houses the motor and control hardware, the pendulum and inertia disk attachments, a USB cable for communication with a computer, and an external power supply. These components are not integrated into a single enclosure and are stored separately when not in use.

### 2.3 Design Requirements

Based on the needs and goals defined by the project sponsors, the following design requirements were selected to guide development. The device must replicate the core functions of the Qube-Servo 2 so that it can be used to complete the same control systems experiments. This includes moving the inertia disk between set angles while accounting for overshoot caused by rotational inertia, as well as balancing the pendulum in the upright position. To support this, the motor and encoder must have similar performance to those used in the Qube-Servo 2, and the system must be able to collect and transfer data at speeds that match or exceed the existing device. All aspects of the device must be open source. This includes CAD files, electrical layouts, code, and assembly instructions. These materials must be publicly available in a GitHub repository so that the device can be reproduced without relying on proprietary information. Cost is a major requirement. The Qube-Servo 2 costs about $5000 per unit, and the target for this project is about $1000 per unit. This requires careful selection of components and manufacturing methods while still meeting performance needs. The device must be self-contained, with all parts stored together in a way that prevents loss or damage. It should not rely on loose storage such as a cardboard box. The system must also be protected during transport and be easy for students to carry between locations. The system must be compatible with MATLAB and Simulink, and the software must be reprogrammable so it can be updated over time as these tools change. It should also be easy to perform maintenance, with components that can be accessed and replaced without difficulty. All parts must be able to be manufactured by third-party vendors, with final assembly completed by the end user using the provided documentation.

## 3 Design Description

### 3.1 Overview

The design maintains the core functionality and accessory compatibility of the Qube-2 while reconfiguring the system into a portable, self-contained unit. Instead of a cube intended for stationary tabletop use, the device is integrated into a protective case that supports transport, storage, and operation within a single structure. The case incorporates features to support use and organization, including a deployable mounting platform and internal storage for attachments and cables. The internal structure is fixed within the case to maintain alignment and stability during operation.

The device is used by students in a control systems course to implement and test real-time control algorithms. A laptop is connected to the device, and Simulink is used to develop programs that control the motor based on project objectives. These programs process sensor data that tracks motor position and generate corresponding control responses in real time.

The device supports two primary attachments. The first is an inertia disc, which is used to study angular position control while accounting for overshoot resulting from the disc’s angular momentum. The second is a pendulum attachment that includes an additional sensor to track its angular position. This configuration is used for control problems where motor motion is adjusted to maintain the pendulum in an upright (inverted) position.

### 3.2 Detailed Description

The final device is shown in Figure 1. In this figure, the device is shown in its operation position with all subassemblies installed.

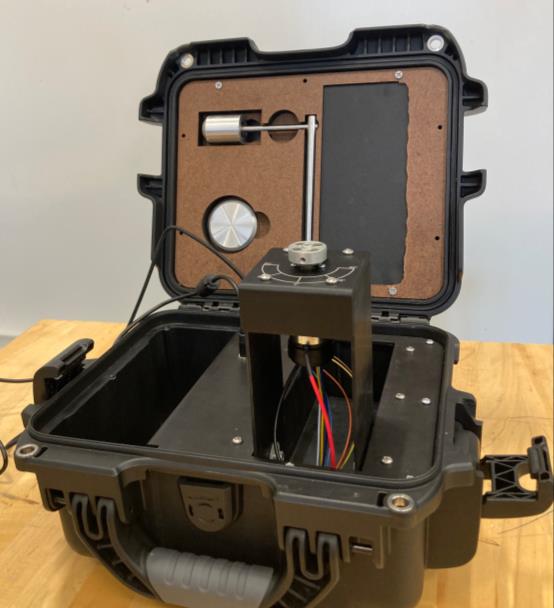
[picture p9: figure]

Figure 1 Image showing the full final design

The device is contained in a Nanuk 905 case, which can be closed and latched for storage and transportation. The lid of the case contains a storage compartment to store the device attachments when not in use. The cavity on the left-hand side of the device is used to store the power supply and data cable. The front panel includes the power and data ports, and also the motor housing.

A close-up view of the attachment storage compartment is shown in Figure 2.

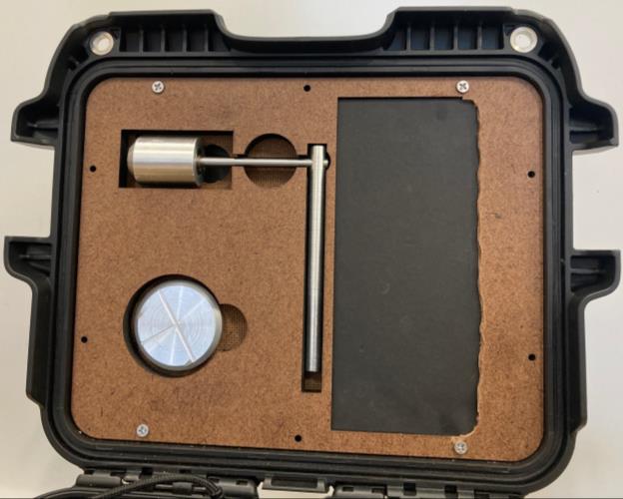
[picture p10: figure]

Figure 2 Image showing the attachment storage compartment

The storage compartment contains two cavities, one for the inertia disc attachment and one for the pendulum attachment. While being stored, the attachments are fixed in place using magnets. The compartment is made up of two layers of hardboard with a layer of foam in between. The top layer of hardboard is mounted to the case, and the foam and the other hardboard layer are attached using glue.

A view of the device in its storage state from above is shown in Figure 3.

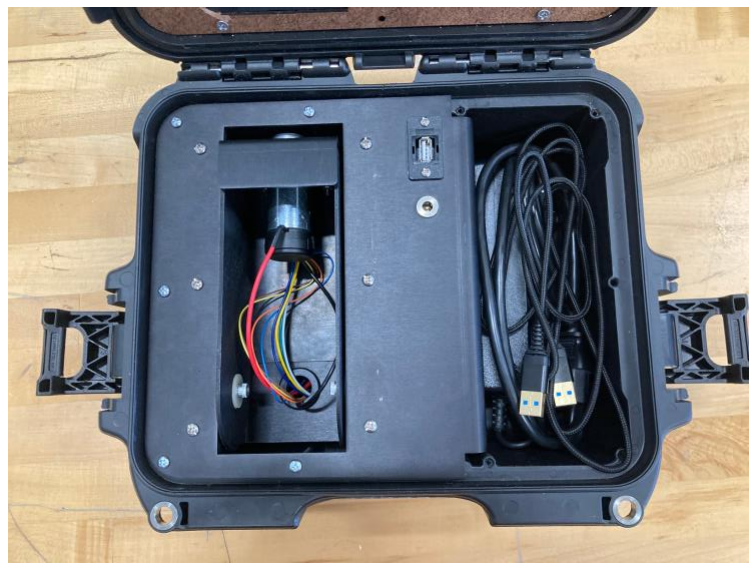
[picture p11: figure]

Figure 3 Device in its storage state

As can be seen in this image, the motor housing is capable of folding down into a trough, which allows the lid to close for storage. To the left of this is a power port and a USB port, where the student would connect their device to their laptop. The cavity on the left, where the USB cable and power supply are stored, is divided from the rest of the internal section of the device with a section of the top panel that is bent down to create this division. This panel is made of anodized aluminum and is screwed to the Nanuk case.

Figure 4 depicts the electrical compartment, located behind the divider that forms the storage cavity.

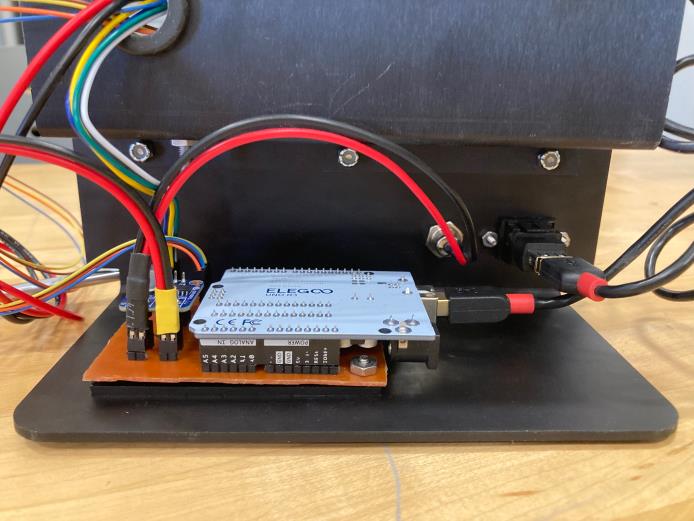
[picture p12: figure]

Figure 4 Electrical compartment of the device

The electrical compartment contains an Arduino, which is used as the microprocessor to control the device. A motor driver is also housed in this compartment and controls the voltage applied to the motor based on an input signal. Both the Arduino and the motor driver are connected to the printed circuit board (PCB). The PCB acts as a junction between the motor and encoder sensors and the motor and consolidates the wiring of the circuit. The Arduino and motor are both directly plugged into the PCB, and the PCB is mounted to the backside of the storage cavity divider with an acrylic plate on the back to insulate the signals in the PCB from the aluminum panel.

The motor housing is shown in the two images displayed in Figure 5.

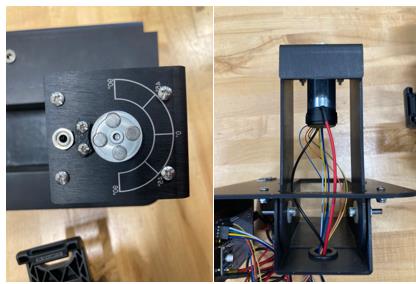
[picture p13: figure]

Figure 5 Top view of the motor housing (left) and side view of the motor housing (right)

In the image on the left, the top of the motor housing, which contains a motor mounting plate that has a built-in handle, can be seen in the right image. The mounting plate has a protractor engraved on it to help demonstrate the control the device has over the inertia disc attachment. The motor is mounted to the bottom of this plate. An attachment interface component is attached to the end of the motor shaft, which utilizes magnets to affix the attachments. There is a 3.5 mm jack port on the plate, which allows the encoder in the pendulum attachment to be connected to the device while in use. The small semicircular component next to the motor is attached to the motor plate to protect the pendulum from swinging too far and damaging the wiring. Below the motor plate are the two motor housing legs, which are used to elevate the motor to allow the pendulum to swing freely while in use. The motor legs are then attached to the trough within the main device using a combination of nylon washers, nuts, and partially threaded bolts, which work as a friction-resistant hinge, keeping the motor housing in place while in the vertical and horizontal positions.

The two device attachments are shown in Figure 6.

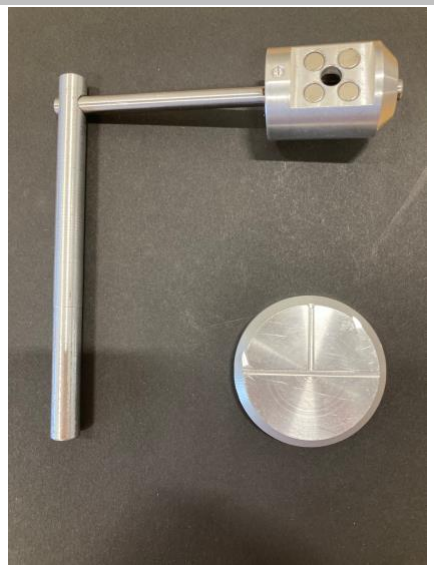
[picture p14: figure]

Figure 6 Image of the two device attachments

On the bottom right is the inertia disc. This disc is solid aluminum and is attached to the device to add inertia to the motor. On the front, there are lines cut into the material that are used to help the observer track the position of the motor and see physically what the device is doing. The disc has magnets inserted into holes on the back, which allow the attachment to be mounted to the mounting interface on the motor. The pendulum consists of 3 major components and some hardware. The pendulum cylinder is the component that attaches to the motor via the attachment interface with the magnets that can be seen in the image. The pendulum axle runs through bearings that are press-fit into the ends of the cylinder and are secured using retaining rings. The pendulum encoder is then mounted to one end of the pendulum cylinder and tracks the position of the pendulum axle. This encoder is connected to a 3.5 mm plug that plugs into the jack on the motor plate when in use. This is not shown in the image, as it was determined that it was not worth wasting an encoder for a pendulum attachment that would not be used. On the far end of the axle is the pendulum arm, which is fixed to the axle using a set screw and creates a moment that causes the pendulum to rotate when out of perfect alignment.

### 3.3 Use

The device is used in a control systems lab to implement and test real-time feedback control algorithms. A laptop is connected to the system, and Simulink is used to write and deploy control programs that interface with the motor and encoders. The system runs in a closed loop, with encoder data fed back to the controller so motor input can be updated in real time.

The first application uses the inertia disc attachment for angular position control. The motor moves the disc between set positions while accounting for inertia and limiting overshoot. This is used to tune PID controllers and observe closed-loop response.

The second application uses the pendulum attachment. The controller moves the pendulum from a downward position to an upright position and maintains it there. This inverted pendulum setup is used to study system stability and disturbance response.

Across both cases, the device is used to connect control theory developed in simulation with a physical system.

## 4 Design Evaluation

### 4.1 Overview

This section outlines how the final design was evaluated against the requirements defined in the problem definition section to ensure that the final device meets the sponsor's expectations for the project. The key requirements and corresponding evaluation methods are summarized in Table 4.1.

Table 4.1 Design Requirements, Test Methods, and Targets

Requirements | Target Value | Testing Method
Qube Function Replication | Pass | Complete Qube Servo 2 Tasks
Motor and Encoder Performance | Comparable | Qube response comparison
Accurate Data Transmission | Pass | Send and receive data
Cost Target | < $1,000.00 | Hand Calculation
Self-Contained Storage | Pass | User Testing
Transport Protection | Pass | User Testing
Portability | Pass | User Testing
MATLAB/Simulink Compatibility | Pass | MATLAB/Simulink Connection
Software Updatability | Pass | Code Modification
Third-Party Manufacturability | Pass | Procurement Validation

### 4.2 Evaluation of Design Criteria

### 4.2.1 Qube Function Replication

Purpose

Evaluating whether the device replicates the functionality of the Qube-Servo 2 is critical to determining overall project success. The objective is to assess whether the system can support the same control experiments performed in the control systems course. If the device cannot reliably execute these experiments, it cannot serve as a replacement.

Test Methods

First, an angular position control project is tested using the inertia disc attachment. A Simulink program is developed to move the disc between specified angular positions (e.g., from 1 rad to −1 rad), with the expectation that the system will reach each position with limited overshoot and briefly stabilize before reversing direction.

Second, a vertical pendulum balancing project is defined. In this test, the pendulum attachment is used, and a Simulink program is designed to swing the pendulum from a downward position to an upright position and maintain it there through continuous motor adjustments. Successful completion requires stable balancing in the inverted position.

Results

The inertia disc test was performed, but was not successful. The microcontroller used in the design, an Arduino, operates with a data transmission rate approximately an order of magnitude slower than the proprietary controller used in the Qube-Servo 2. This limitation introduced a significant delay in the control loop.

As a result, the system was unable to respond to position feedback in a timely manner. During testing, when commanding motion between 1 rad and −1 rad using a PID controller, the motor consistently overshot the target position by a large margin. In some cases, the motor position exceeded 100 rad before reversing direction. This behavior indicates that the controller was acting on outdated position data, leading to excessive acceleration and instability.

Due to the failure of the inertia disc test, the pendulum balancing test was not attempted. The inverted pendulum problem requires faster and more precise control than basic angular position regulation, and there was no indication that the system would perform adequately under those conditions given the observed limitations.

Overall, the device does not replicate the functional performance of the Qube-Servo 2 and does not meet the requirements for use in the intended control systems experiments.

### 4.2.2 Motor and Encoder Performance

Purpose

This test evaluates the motor and encoder response of the system to determine whether it can support control systems instruction. Accurate and repeatable motion tracking is required, and performance is expected to match the Qube-Servo 2 under equivalent conditions.

Test Methods

A Simulink-based motion profile is executed on both the device and the Qube-Servo 2. Each system is commanded to follow the same set of position changes over time, and encoder position is recorded and plotted for comparison against the input trajectory.

Performance is assessed by comparing how closely each system tracks the commanded motion in similar operating conditions. The device is expected to meet or exceed the tracking accuracy of the Qube-Servo 2 for this test to pass.

Results

This test is dependent on the system’s ability to replicate the core functionality of the Qube-Servo 2 under closed-loop control conditions. As identified in Section 4.2.1, the device was not able to achieve equivalent performance in the inertia disc control task due to limitations in the control loop implementation.

Because this test evaluates the same motor and encoder response behavior under comparable operating conditions, the previously observed performance limitations directly carry over. The device is unable to maintain the required accuracy and stability in real-time motion tracking when compared to the Qube-Servo 2.

Based on this, the system does not meet the required performance equivalence for motor and encoder response.

### 4.2.3 Accurate Data Transmission

Purpose

Testing data transmission between Simulink and the Arduino is necessary to determine whether the control systems experiments can be completed successfully. If transmitted data is inaccurate or inconsistent, the inertia disc project will not reach correct target positions, and the pendulum system will not receive correct feedback for maintaining stability.

Test Methods

Data transmission is evaluated by comparing commanded and returned values within Simulink and the Arduino system. The following test cases are used:

1. Bidirectional Simulink-Arduino communication (loopback test)
Simulink sends numerical values to the Arduino, which are immediately returned to Simulink without interacting with hardware components.
This verifies that transmitted values remain unchanged through the communication process.
2. Encoder value transmission to Simulink
Encoder readings are transmitted from the Arduino to Simulink in real time.
This test evaluates whether position data is correctly represented in Simulink without loss or distortion.

3. Motor command transmission (voltage control)
Simulink sends voltage commands to the Arduino to control motor direction and magnitude. The received values are checked against the commanded inputs to confirm correct interpretation and execution.
4. Closed-loop motor control with encoder feedback
Voltage commands are sent to the motor while encoder values are returned to Simulink. This test evaluates whether transmitted command and feedback signals remain accurate when operating together in a full control loop.

Results

1. Pass
2. Pass
3. Pass
4. Pass

### 4.2.4 Cost Target

Cost Objective

Cost was one of the primary constraints for the project. The Quanser Qube-Servo 2 costs $5000 per unit, and the target for this design was to keep the cost below $1000 per unit. This requirement is critical because the value of this project must replicate the functionality of the Qube 2 and do so at a realistic cost for universities to adopt and reproduce the system at scale. A device that performs well but remains too expensive to replicate would not meet the intent of the project.

For this reason, success in this section is defined by whether the final design can be reproduced at or below the $1000 target per unit. Prototype development costs are considered separately, as they include one-time expenses and inefficiencies that do not represent final production.

Methodology and Assumptions

The cost of the system was evaluated from the perspectives of total research and development cost for the prototype and projected per-unit cost assuming a production run of ten units. The R&D cost includes all expenses related to components, manufacturing, and design iterations, and reflects the true cost of development. The projected per-unit cost was calculated using a finalized bill of materials, supplier quotes, and known manufacturing costs. Batch production was assumed where applicable, particularly for attachment and housing components, reducing per-unit cost compared to prototype manufacturing. Labor and assembly were not included, and prototype-specific costs such as duplicate purchases and redesigned iterations were excluded.

Resulting Budget

The estimated per-unit cost for the final design is $763.68, well below the $1000 target, providing a margin of roughly $236. This indicates the design meets cost requirements and is significantly more affordable than the Qube-Servo 2.

Total research and development cost is $1739.75, compared to a running estimate of $1187.00. The higher true cost is mainly due to manufacturing costs. Originally estimated around $280.00, a figure closer to $1000 is more realistic due to low-volume production and design iteration. Additional increases came from motor selection changes and higher electrical component costs. Despite this, the projected production cost remains within the target, as prototype inefficiencies such as one-off manufacturing and duplicate purchases would not apply to batch production. Overall, while development costs exceeded initial estimates, the final design meets the cost objective and remains economically viable.

### 4.2.5 Self-Contained Storage

Purpose

The Quanser Qube-Servo 2 is made up of five components that are all loose and currently stored together in a cardboard box. The device designed for this project solves this issue by being built in a case with storage compartments to fit all of the loose components. If even one of these components is unable to be stored in the case, it would defeat the purpose of building the device within a case.

Test Methods

All the loose components of the device: the 2 attachments, the power supply, and the computer connection cable, will be placed in their respective storage locations. If the case can be closed without damaging any of the components, the device will pass the test.

Results

The first prototype of the device was tested by placing only the power supply and computer connection cable in the storage compartment, and it was determined that the compartment was too small to accommodate these components. This was increased in the second iteration, which had a large enough compartment to accommodate the cords. When the attachment storage compartment in the lid was added to the device, the attachments were placed in their respective locations, the cords were placed in their storage compartment, and the lid was closed. The lid was able to close completely, and the Nanuk case was successfully latched shut, indicating that the device passed the test.

### 4.2.6 Transport Protection

Purpose

The device contains many components that can be easily damaged if exposed to water, if they are bumped, or dropped, and so it was decided to integrate the device within a Nanuk 905 case to protect these delicate components from getting damaged. The extent to which this case will protect the internal components will not be tested, as destructive testing is not within the budget of this project. The Nanuk 905 case is, however, certified to protect contents from rain and drops as per ASTM D-4169 DC-18. The certification that this case has will be assumed to ensure the safety of the internal contents.

### 4.2.7 MATLAB/Simulink Compatibility

Purpose

Being able to connect the device to MATLAB/Simulink allows data to be transferred between the controlling script written by the student and the Arduino within the device. Compatibility with MATLAB/Simulink is critical to the function of the device, and the project will not be successful without it.

Test Methods

An Arduino code was created that uses serial transmission and a receiver, along with a MATLAB Systems Simulink block that can utilize serial communication to confirm that signals can be transmitted in both directions. The test will be successful if the values are sent from Simulink to Arduino and then returned, and the values received at the Arduino and returned to Simulink match the original value.

Results

The test values were sent, and the values received at the Arduino and received in Simulink matched the values that were sent, which means the device passed the test.

### 4.2.8 Software Updatability

Purpose

A known limitation of the Qube-2 system is that it only operates reliably with older versions of MATLAB and Simulink, creating compatibility issues for current classroom use. This project aims to ensure the device functions on modern and recent software versions without requiring extensive configuration or troubleshooting. The goal is a straightforward setup process where the system can be used directly in a typical control system.

Test Methods

Initial testing involved running the MATLAB, Simulink, and Arduino code on the latest software version as well as several recent supported versions. When issues were encountered on the most recent release, testing was adjusted to evaluate compatibility on earlier versions instead. The modified test focused on verifying correct motor voltage control and encoder-based position tracking using Simulink across those versions.

Results

The system did not operate correctly on the latest MATLAB and Simulink release, requiring a revision of the test approach. On earlier supported versions, the device was able to successfully control motor voltage and accurately track position using encoder feedback. Behavior was consistent across the tested older versions, with no observed data or control issues. Based on these results, the system is considered compatible with prior supported software versions. It is also expected that future compatibility can be maintained with minor code or syntax updates as software versions change. Based on these results, the device passes the test.

### 4.2.9 Third-Party Manufacturability

Purpose

The sponsors of this project would like all the components of the device to be able to be manufactured by third-party companies, so that all parts can be ordered and then just assembled. This will also mean that any other individuals who are interested in replicating the device will be able to just order all the components and follow the assembly instructions to complete the device.

Test Methods

All components required to build the device will be ordered by third-party manufacturing companies, and if a suitable component is received for each of these components, the device will pass this test.

Results

In the first two prototypes, issues with the manufacturability were found and subsequently solved. All parts that have been received at this point have been confirmed to be manufacturable. This includes the main plate, the trough, the motor housing legs, and the motor plate.

### 4.2.10 Device Evaluation Summary

The device meets several key requirements, including accurate data transmission, MATLAB/Simulink compatibility, open-source documentation, cost targets, self-contained storage, transport protection, and software updatability on supported versions. These results show the system is usable, reproducible, and deployable in a control systems lab with minimal setup. The design also performs well in packaging and integration, with all components successfully stored and protected within the case.

The device does not achieve functional equivalence with the Qube-Servo 2 in closed-loop control performance. The inertia disc test failed due to limitations in the control loop, which affected motor and encoder performance under dynamic conditions. As a result, the inverted pendulum test was not completed. Ease of maintenance is assumed to pass based on planned instruction manual revisions and user testing. Overall, the device meets most implementation requirements but does not meet the performance requirements for full replacement of the Qube-Servo 2.

### 4.3 Conclusions

The final design addresses many of the implementation and usability goals established at the beginning of the project. The device was redesigned into a self-contained portable device that integrates storage, protection, and operation into a single system while using similar attachments as the Qube-2. The system met several major project requirements, including accurate data transmission, MATLAB/Simulink compatibility, open-source documentation, manufacturability through third-party vendors, and meets the overall cost target. The projected production cost of approximately $764 per unit is significantly lower than the cost of the Qube-Servo 2, demonstrating that a much more affordable alternative can be developed while keeping and improving many of the same functional and educational features.

The physical design of the device was effective for the presentation and mechanical function of the device. The integrated Nanuk case successfully stores and protects all system components, improving portability and organization compared to the existing Qube-Servo 2 design. The modular assembly process and open-source hardware and software support long-term maintainability and reproducibility for future users or institutions.

Despite these successes, the project did not fully achieve the primary performance objective of replicating the operational functionality of the Qube-Servo 2. Testing showed that the Arduino-based control system was unable to process and transmit feedback data at the speed required for stable real-time control. This resulted in significant delays between input and output during inertia disc testing, preventing the successful completion of the intended control experiments and making pendulum balancing impossible with the current hardware configuration. Because of this limitation, the device cannot yet serve as a complete replacement for the Qube-Servo 2 in its current form.

Overall, the project demonstrated that a low-cost, open-source, and manufacturable control systems teaching platform is feasible. The results also identified the primary technical limitation preventing full success, providing a clear direction for future development. Replacing the current microcontroller with a faster platform and retesting the system would likely allow the design to achieve the required closed-loop performance needed to operate the pendulum, while retaining the strengths of the existing mechanical and electrical architecture.

### 4.4 Next Steps

The next step in the project is to address the primary limitation identified in testing, which is the performance of the Arduino microcontroller. A replacement microcontroller with higher data handling capability needs to be selected and integrated into the existing system architecture. Once integrated, the full system should be retested using the same control experiments that were previously used, including the inertia disc and pendulum tests, to confirm that the updated control loop meets the required performance and resolves the instability observed in this iteration.

After the system successfully passes these tests, the remaining steps can proceed as planned. This includes cataloging all existing components from the prototype phase to ensure reusable parts are not wasted. A small production run can then be assembled using ordered components, with assembly completed in batches by sophomore or junior mechanical or electrical engineering students following the finalized instruction manual. Each completed unit should undergo functional testing before deployment, and a prototype unit should be provided to the course instructor for preparation and integration into the control systems curriculum.

## 5 Appendix

### 5.1 Quanser Qube-Servo 2 Specifications Table

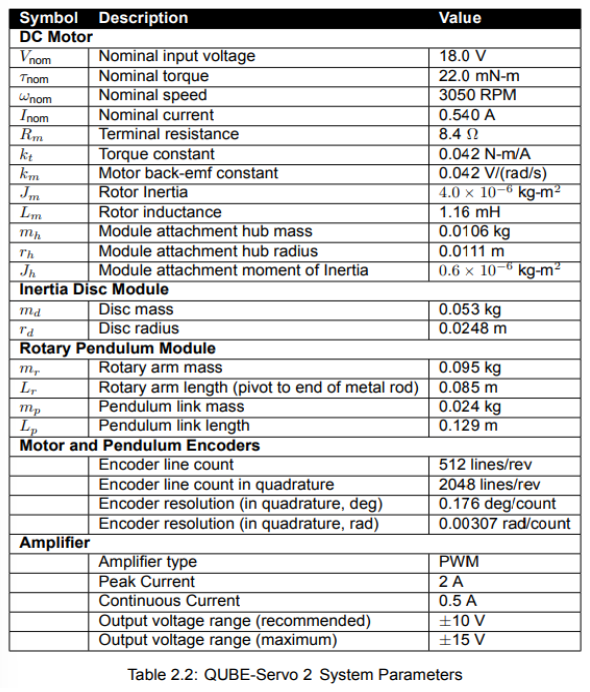
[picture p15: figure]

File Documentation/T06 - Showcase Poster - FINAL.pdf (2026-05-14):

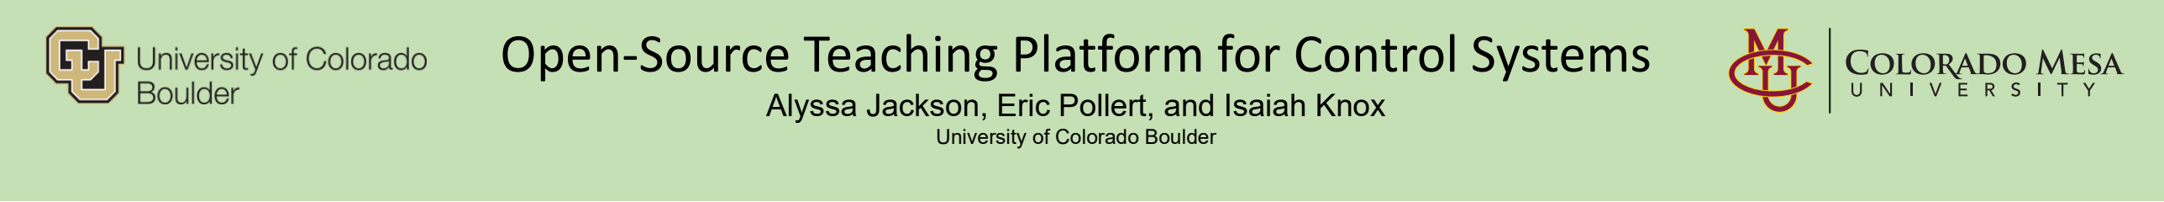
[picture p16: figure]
University of Colorado Boulder

# Open-Source Teaching Platform for Control Systems

### Alyssa Jackson, Eric Pollert, and Isaiah Knox

## Problem Definition

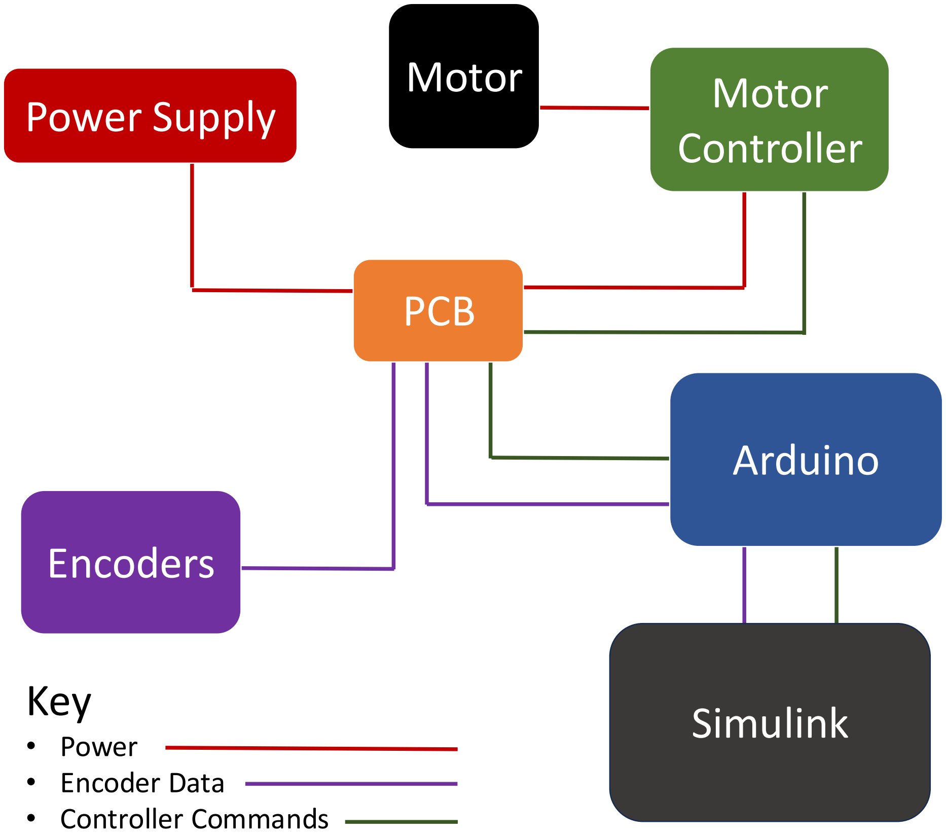
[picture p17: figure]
Power Supply; PCB; Arduino; Encoders; Motor Controller; Motor; Simulink; Key; • Power • Encoder Data • Controller Commands
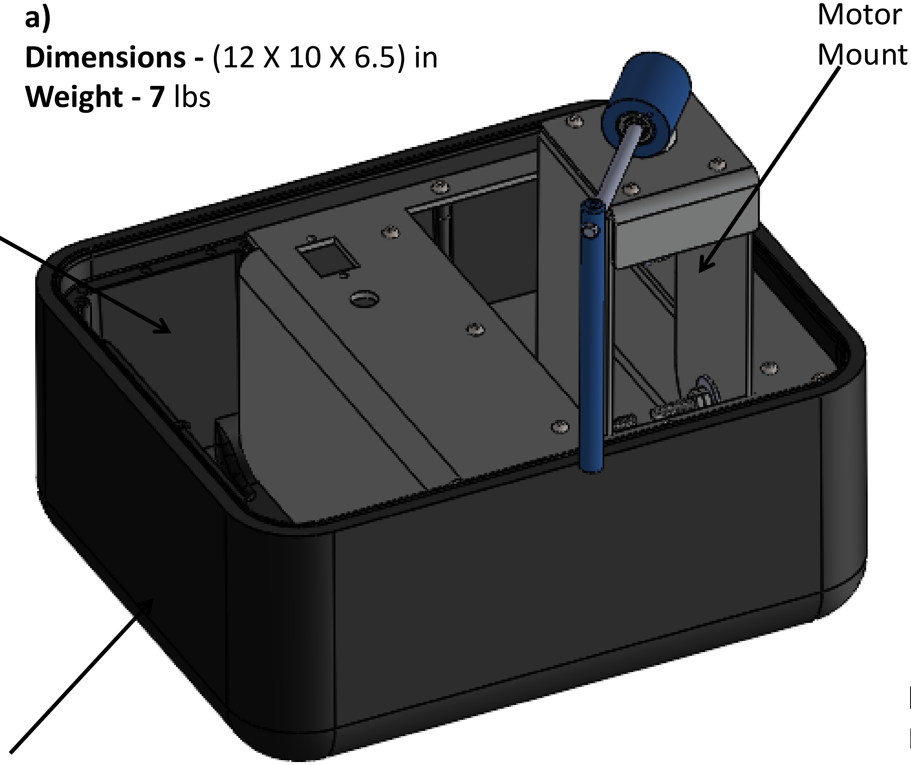
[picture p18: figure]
Motor Mount; a) Dimensions - (12 X 10 X 6.5) in Weight - 7 lbs
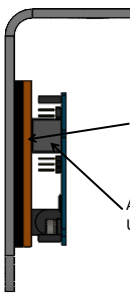
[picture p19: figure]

## Design Requirements

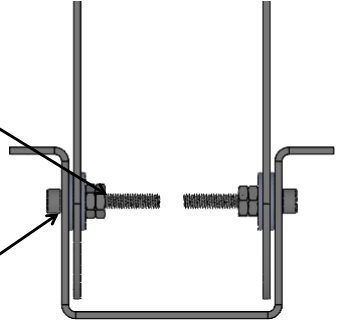
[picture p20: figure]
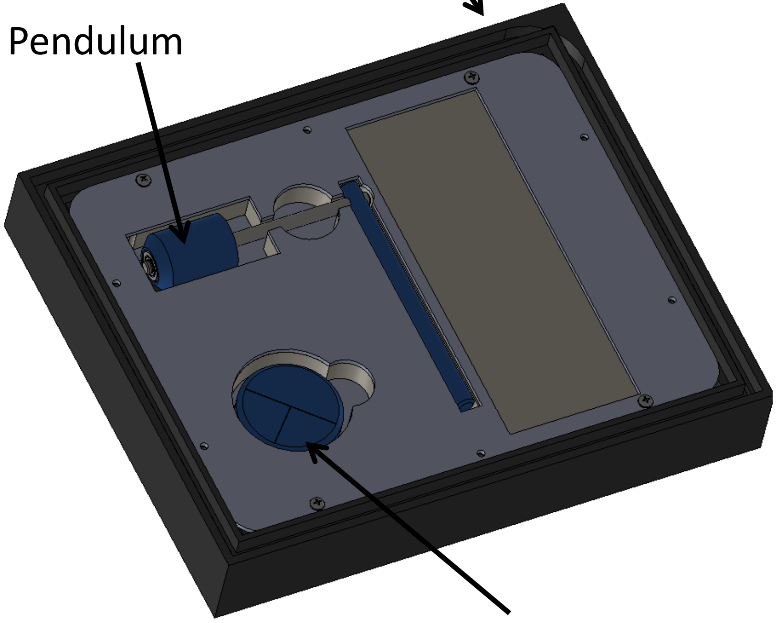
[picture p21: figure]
Pendulum

Project Sponsor: Dr. Nathan McNeill and Dr. Talles Santos | Acknowledgments: Jeremy Bergen, Bob Wilson, Karl Castleton, Dr. Fransico Castro, and Christopher Pennick.

## Design Evaluation

## Design

- Replicate all major functions of Qube-Servo 2
- Open-source
- Easy for students to carry around
- Able to be updated to work with future software versions
- Easy to take apart for maintenance and modification
- Control Systems utilizes Quanser Qube-Servo 2 as a teaching platform.
- Drawbacks of the Qube-Servo 2
- Costs $5,000 per device
- Requires outdated software
- Not easily portable
- Requires proprietary software
- The Partnership Program only owns six
- The Electrical and Computer Engineering Program desires to increase the number of devices available.

## Electrical Design

## Conclusions

## Next Steps

- Development costs totaled to $2,000
- Production costs estimated to be $862.25 per unit
- System communicates data with speed and accuracy
- Storage and portability are improved in comparison to Qube-Servo 2
- Critical function and performance testing still in progress
- Final success depends on matching the functionality of the Qube-Servo
Requirements | Testing Method | Results
Qube Function Replication | Complete Qube
| Servo 2 Tasks | Pending
Motor and Encoder Performance | Response
| Comparison | Pass

Data Transmission
Speed | Response Timing | Pass
Open Source Documentation | Documentation
| Review | Pending
Cost Target | Hand Calculation | Pass
Self-Contained Storage | User Testing | Pass
Transport Protection | User Testing | Pass
Portability | User Testing | Pass
MATLAB/Simulink Compatibility | MATLAB/Simulink
| Connection | Pass

Software Updatability Code Modification Pending
Ease of Maintenance | User Testing | Pass
Third-Party Manufacturability | Procurement
| Validation | Pass
- Consolidate documentation, code, schematics, and instructions on GitHub.
- Catalog extra components remaining from research and development for reuse.
- Order parts for a small production run.
- Assemble units in batches using the provided instructions.
- Test each unit and prepare for classroom use.

Figure 1: Control Systems Teaching Platform
a) Full Assembly
b) Electronic Compartment
c) Lid Assembly
d) Hinge Assembly

Power Supply
Storage

Arduino
Uno R3

PCB

Inertia Disk

NANUK 905 Case

Partially
Threaded Bolt

Nylon
Washers

Figure 2: Block diagram of the electrical communication of the Control Systems Teaching Platform
b)
Dimensions - (1.5 X 4 X 7) in

d)
Dimensions - (2.5 X 2.5 X 7.5) in

c)
Dimensions - (12 X 10 X 2) in

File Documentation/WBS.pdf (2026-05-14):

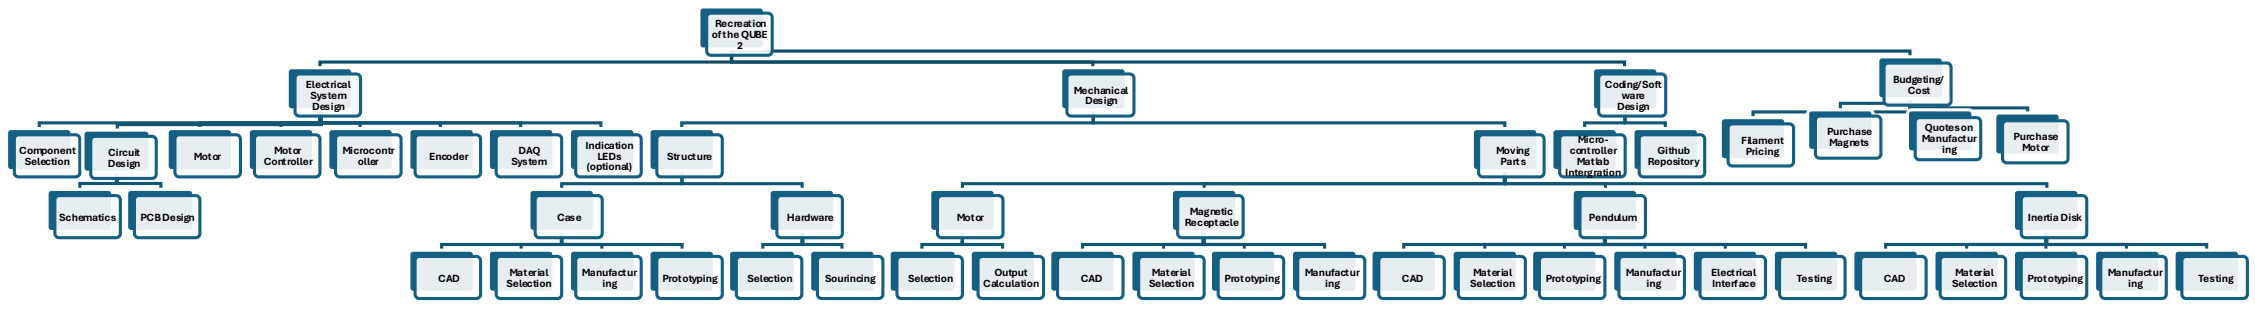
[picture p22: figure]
Recreation of the QUBE 2; Budgeting/ Cost; Quotes on Manufactur ing; Filament Pricing; Purchase Magnets; Purchase Motor; Electrical System Design; Component Selection; Circuit Design; Schematics; PCB Design; Motor; Controller; Microcontr; oller; Encoder; DAQ; System; Indication LEDs (optional); Mechanical Design; Structure; Case; CAD; Material; Selection; Manufactur; ing; Prototyping; Hardware; Sourincing; Moving Parts; Output; Calculation; Magnetic Receptacle; Pendulum; Electrical Interface; Testing; Inertia Disk; Material Selection; Manufactur ing; Coding/Soft ware Design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

Project Objective Statement: To redesign and build a product similar to the Qube 2.

# Our product should be easily manufacturable and repairable, able to be upgraded in the future, work on with the latest Matlab software and over various types of computer hardware, and a tool that can be used to reliability teach students control systems

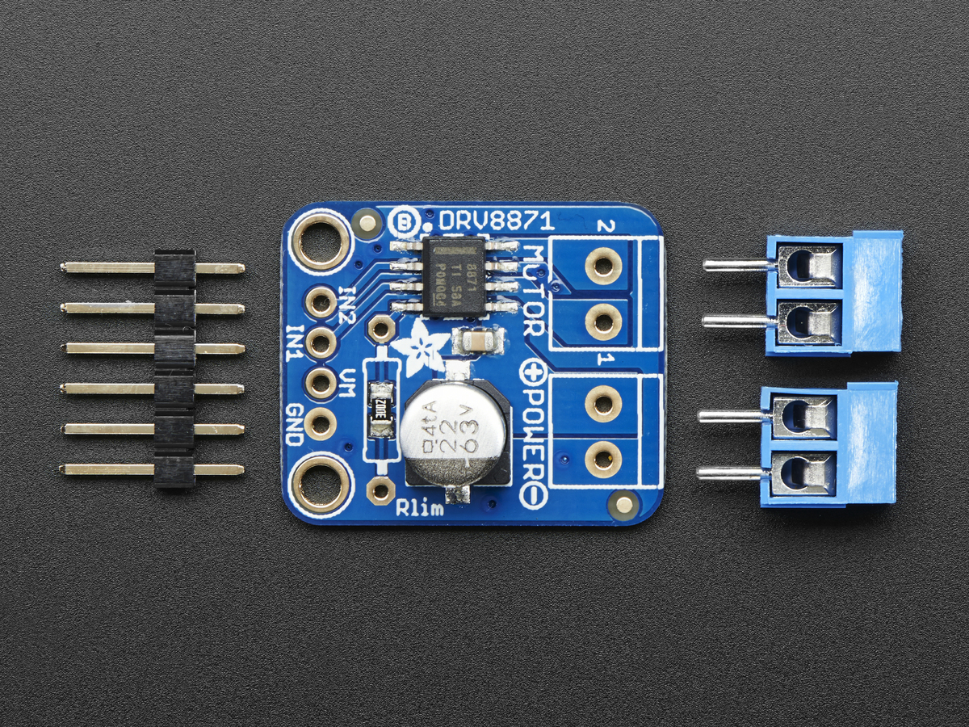
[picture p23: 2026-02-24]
Hardware/PCBModels/library_CAD/Adafruit-DRV8871-Breakout-PCB-master/assets/image.jpg

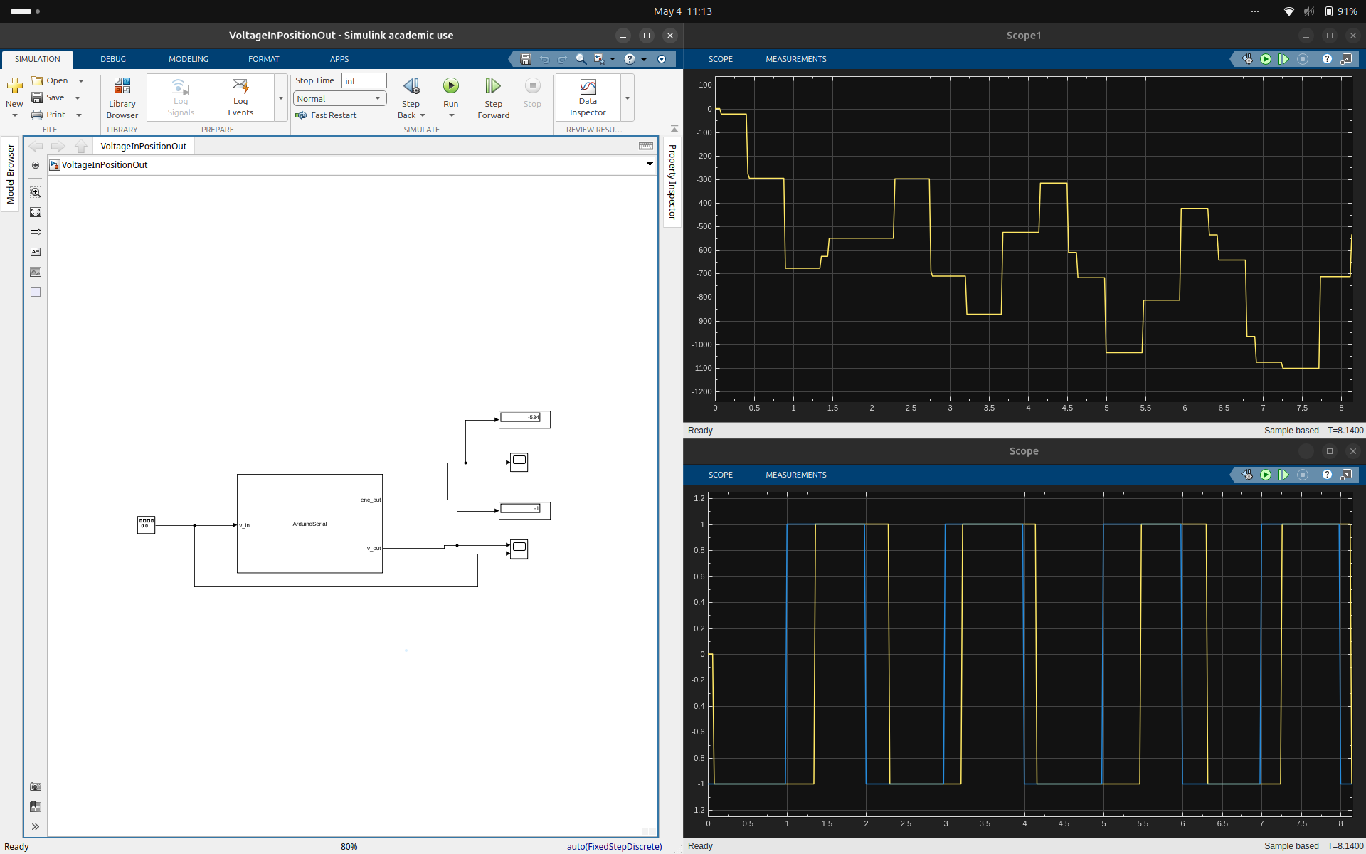
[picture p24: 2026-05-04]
Images/PosistionAndVoltagePlot.png

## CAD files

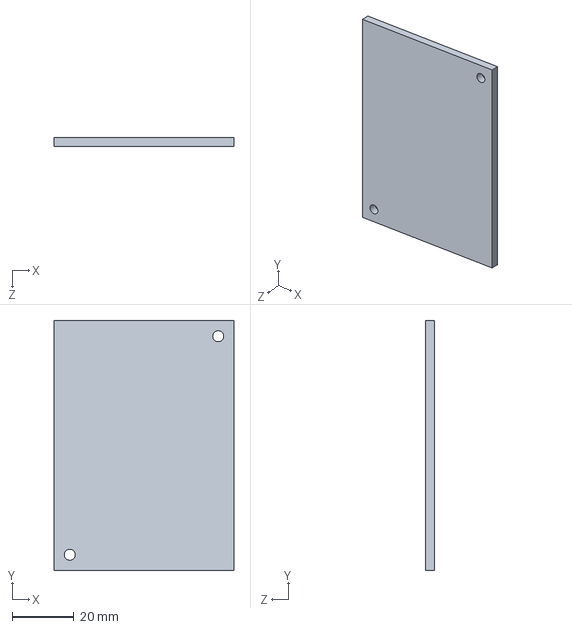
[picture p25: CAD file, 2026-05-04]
Hardware/3DModels/CurrentVersion/Device Components/PCB Mounting Plate.SLDPRT
58.2 x 80.9 x 3.00 mm

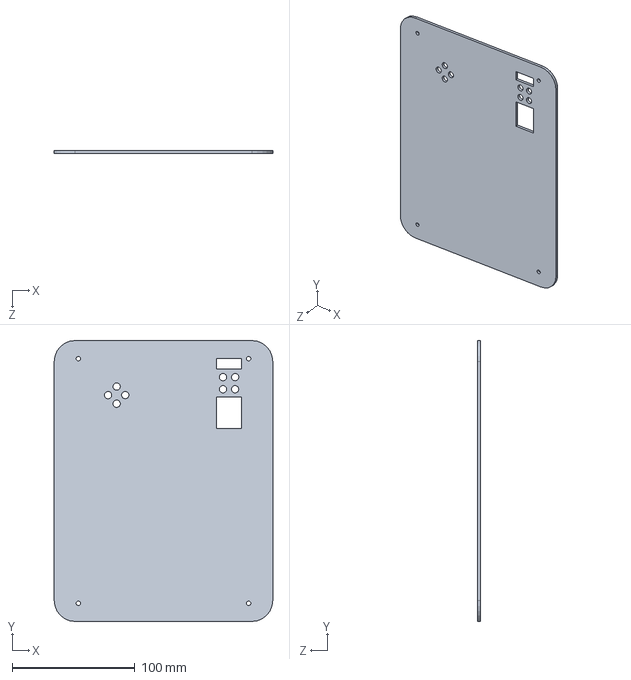
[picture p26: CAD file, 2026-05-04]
Hardware/3DModels/CurrentVersion/Storage Compartment Components/Rear Lid Panel.SLDPRT
177.8 x 228.6 x 2.54 mm

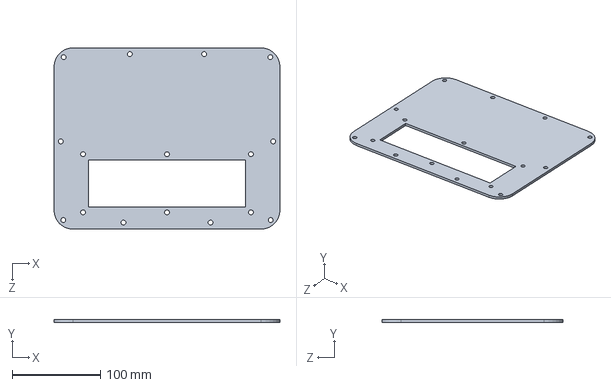
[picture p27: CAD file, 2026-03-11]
Hardware/3DModels/PastVersions/DesignIdea1/Box_plate_idea_1.SLDPRT
256.4 x 3.17 x 205.6 mm

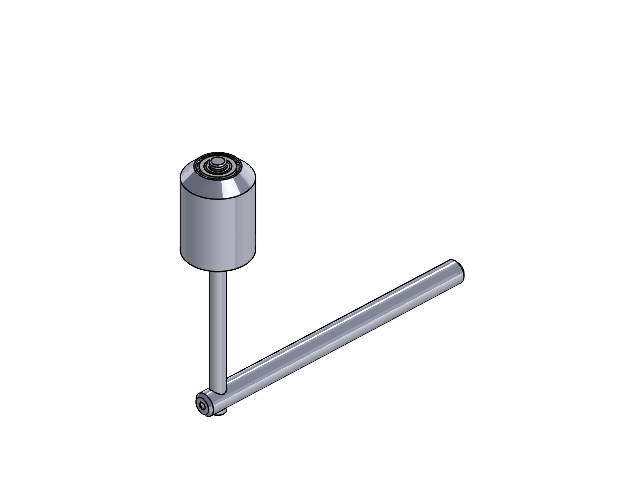
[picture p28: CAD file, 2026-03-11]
Hardware/3DModels/PastVersions/DesignIdea2/Pendulum assembly.SLDASM
Pendulum mount
57155K323_Stainless Steel Ball Bearing x 2
Pendulum shaft
Pendulum Arm

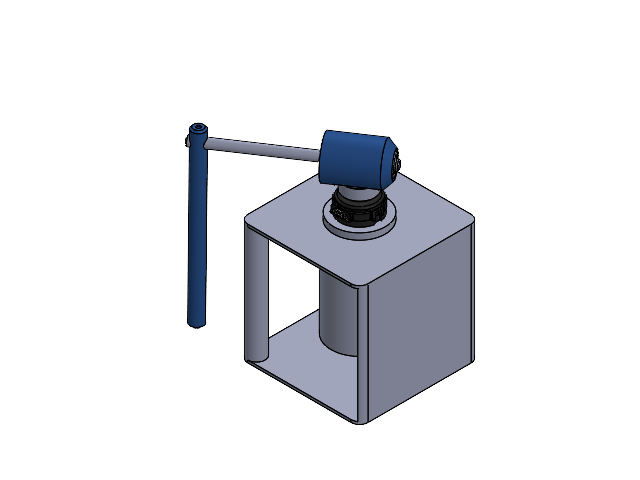
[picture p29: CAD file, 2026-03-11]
Hardware/3DModels/PastVersions/DesignIdea3/Solution_3_Assembly.SLDASM
Enclosure Norm
Motor
Encoder Motor Interface
E8T-X-250-S-H-M-X
V2 Attachment Interface
Pendulum mount
57155K323_Stainless Steel Ball Bearing x 2
Pendulum shaft
Pendulum Arm

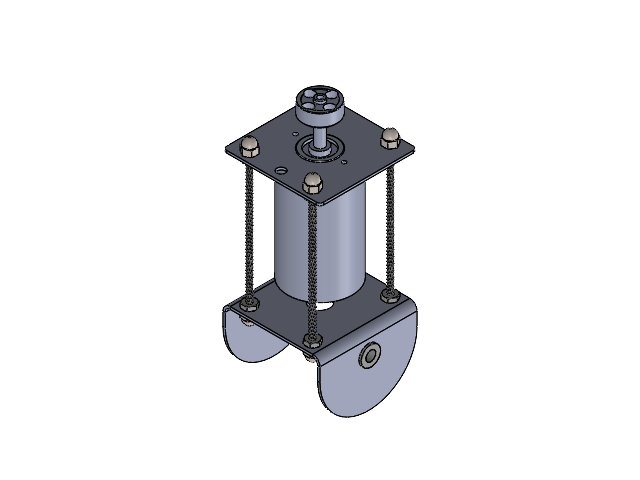
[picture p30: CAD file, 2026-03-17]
Hardware/3DModels/PastVersions/Itteration1/Motor Housing Assembly.SLDASM
bracket
Part6^Motor Housing Assembly
Part7^Motor Housing Assembly
6338K411_Oil-Embedded Flanged Sleeve Bearing x 2
91565A320_Low-Strength Steel Threaded Rod x 4
acorn low crown nut_ai x 8
Motor Plate
Motor
V2 Attachment Interface
90480A007_Low-Strength Steel Hex Nut x 8

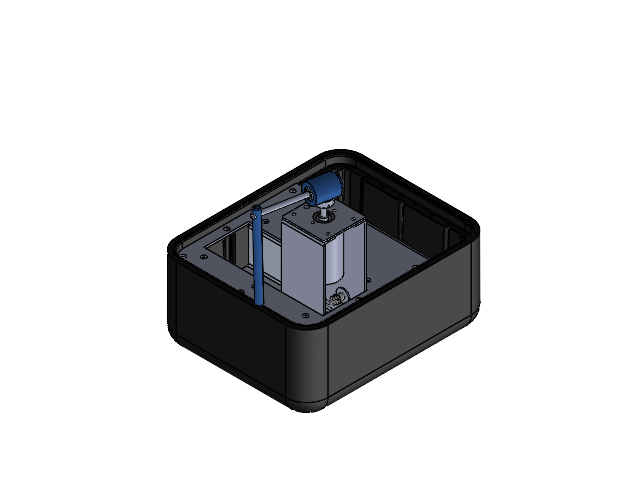
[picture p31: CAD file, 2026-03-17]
Hardware/3DModels/PastVersions/Prototype1/FullAssembly.SLDASM
Case_inner_surface
Plate bend inlet
Housing
Motor Plate
Motor Leg x 2
Motor
V2 Attachment Interface
90128A948_Zinc-Plated Alloy Steel Socket Head Screw x 2
90295A239_Nylon Plastic Washer x 4
92320A753_18-8 Stainless Steel Unthreaded Spacer x 2
90480A195_Low-Strength Steel Hex Nut x 4
Pendulum mount
57155K323_Stainless Steel Ball Bearing x 2
Pendulum shaft
Pendulum Arm

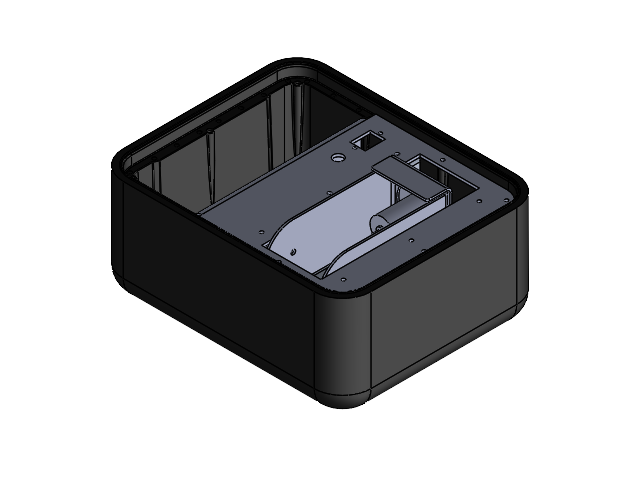
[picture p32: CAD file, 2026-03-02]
Hardware/3DModels/PastVersions/Prototype2/Full Assembly.SLDASM
Case_inner_surface
Plate bend inlet
Housing
Motor Plate
Motor Leg x 2
Maxon Motor
V2 Attachment Interface
Pendulum Stop

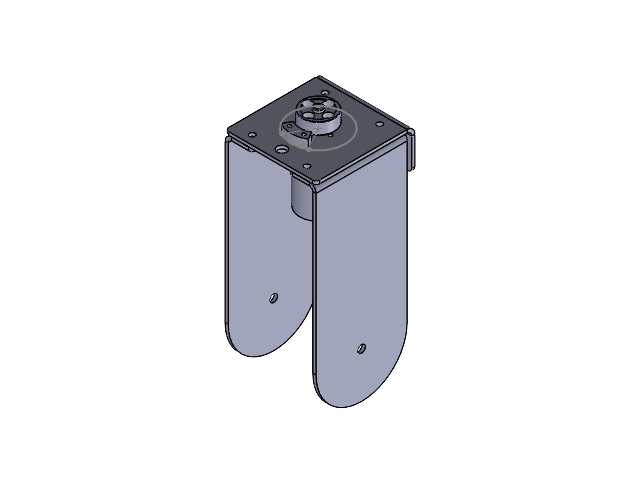
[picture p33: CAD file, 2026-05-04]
Hardware/3DModels/CurrentVersion/Device Components/Motor Arm.SLDASM
Motor Plate
Motor Leg x 2
Maxon Motor
V2 Attachment Interface
Pendulum Stop

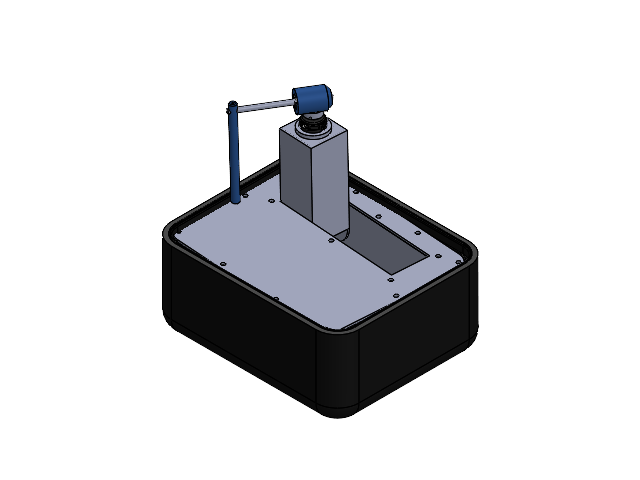
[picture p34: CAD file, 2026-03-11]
Hardware/3DModels/PastVersions/DesignIdea1/Idea_1_assembly.SLDASM
Case_inner_surface
Box_plate_idea_1
Motor_Inlet
MotorStand
Motor
V2 Attachment Interface
Pendulum mount
57155K323_Stainless Steel Ball Bearing x 2
Pendulum shaft
Pendulum Arm
Encoder Motor Interface
E8T-X-250-S-H-M-X

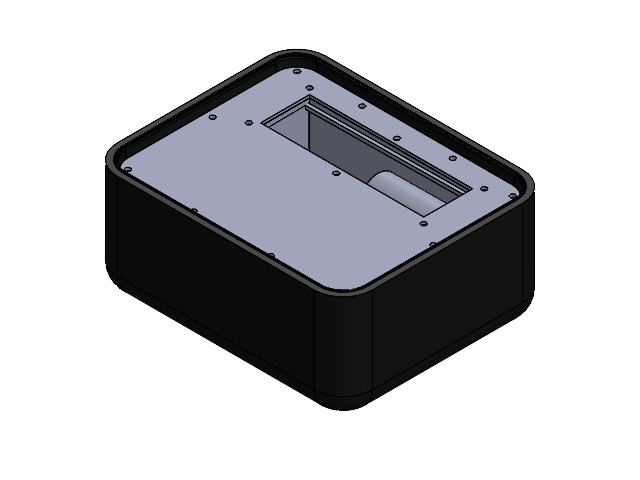
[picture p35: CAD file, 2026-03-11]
Hardware/3DModels/PastVersions/DesignIdea2/Idea_2_Assembly.SLDASM
Case_inner_surface
Box_plate_idea_2
Motor_Inlet_2
MotorStand_2
Motor
Encoder Motor Interface
E8T-X-250-S-H-M-X
V2 Attachment Interface

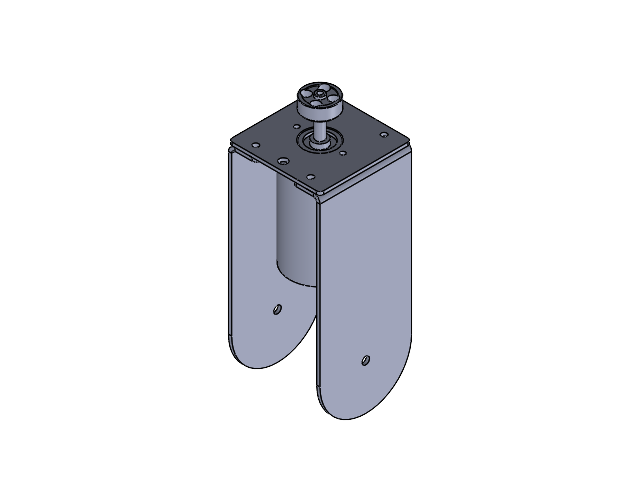
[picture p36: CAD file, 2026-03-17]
Hardware/3DModels/PastVersions/Prototype1/Motor Housing Assembly.SLDASM
Motor Plate
Motor Leg x 2
Motor
V2 Attachment Interface

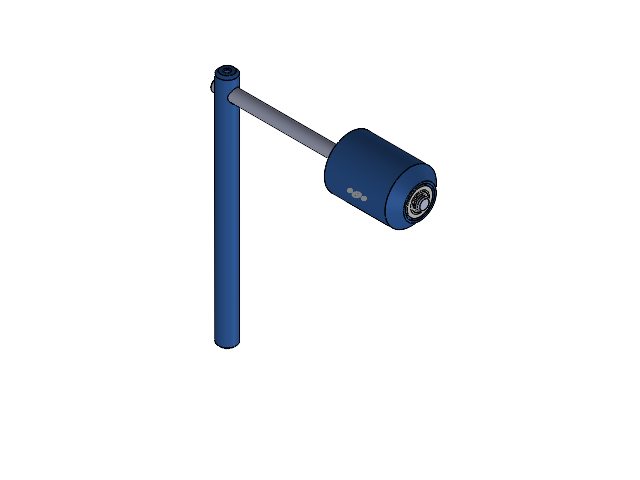
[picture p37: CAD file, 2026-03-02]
Hardware/3DModels/PastVersions/Prototype2/Pendulum Assembly.SLDASM
Pendulum mount
57155K323_Stainless Steel Ball Bearing x 2
Pendulum shaft
Pendulum Arm

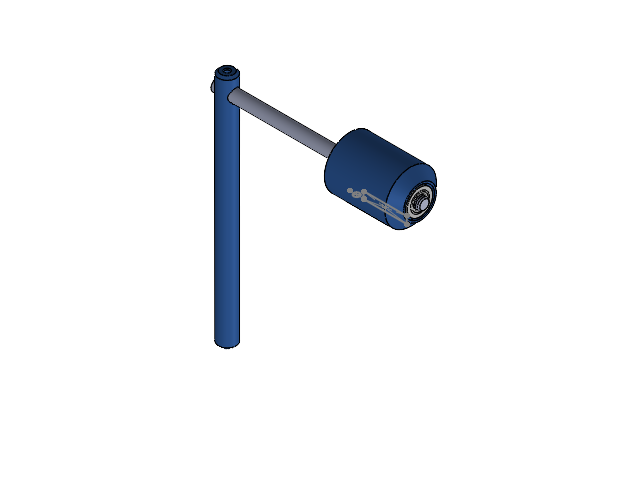
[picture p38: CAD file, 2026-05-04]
Hardware/3DModels/CurrentVersion/Device Components/Pendulum Assembly.SLDASM
Pendulum mount
57155K323_Stainless Steel Ball Bearing x 2
Pendulum shaft
Pendulum Arm

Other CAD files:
Hardware/3DModels/PastVersions/Itteration1/Pendulum assembly.SLDASM
Hardware/3DModels/PastVersions/Prototype1/Pendulum assembly.SLDASM
Hardware/3DModels/PastVersions/Prototype2/Motor Arm.SLDASM
Hardware/3DModels/CurrentVersion/Device Components/Full Assembly.SLDASM
Hardware/3DModels/CurrentVersion/Device Components/57155K323_Stainless Steel Ball Bearing.SLDPRT
Hardware/3DModels/CurrentVersion/Device Components/90128A948_Zinc-Plated Alloy Steel Socket Head Screw.SLDPRT
Hardware/3DModels/CurrentVersion/Device Components/90295A239_Nylon Plastic Washer.SLDPRT
Hardware/3DModels/CurrentVersion/Device Components/90480A195_Low-Strength Steel Hex Nut.SLDPRT
Hardware/3DModels/CurrentVersion/Device Components/Arduino UNO.SLDPRT
Hardware/3DModels/CurrentVersion/Device Components/Attachment Interface.SLDPRT
Hardware/3DModels/CurrentVersion/Device Components/Housing.SLDPRT
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

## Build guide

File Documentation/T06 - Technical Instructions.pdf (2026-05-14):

Open-Source Teaching Platform for Control Systems: Technical Instructions

# Open-Source Teaching Platform for Control Systems:

# Technical Instructions

## Isaiah Knox, Alyssa Jackson, and Eric Pollert

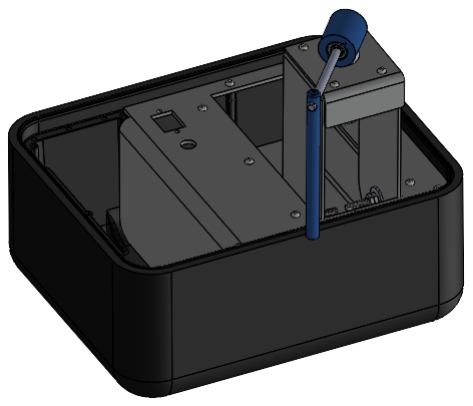
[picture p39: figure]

## Contents

### 1 Introduction | 3

1.1 Scope | 4
1.2 Safety | 4

### 2 Package Contents | 4

### 3 Materials/Tools Required | 5

3.1 Hardware | 6
3.2 Software | 6

### 4 Procedure | 6

4.1 Assembly | 6
4.2 Operation | 6
4.3 Maintenance | 8
4.4 Storage | 8

### 5 Troubleshooting | 8

### 6 Technical Support | 8

### 7 Spare Parts/Components | 8

## 1 Introduction

### 1.1 Scope

This device is a tabletop electromechanical platform developed to support instruction in control systems classes. It is intended for use in undergraduate laboratories where engineering students design, implement, and evaluate feedback control strategies such as PID control on a physical system rather than in simulation alone.

The system is designed to replicate the functional behavior and key performance characteristics of the Quanser Qube-Servo 2 so that existing laboratory exercises and workflows can be maintained without modification. Core components, including the DC motor and optical encoders, are used to create a response in the motor based on feedback from the encoders. This allows the device to serve as a drop-in replacement for the Qube-Servo 2 in control systems classes, as it consists of the same major components and is capable of completing the same tasks.

This device was created as an open-source alternative to the Quanser Qube-Servo 2. All design schematics, code, and documentation are available on GitHub to anyone interested in utilizing this device. This approach is intended to prevent obsolescence tied to proprietary software or hardware dependencies and to allow future updates as course requirements or supporting technologies evolve.

These instructions describe the configuration, assembly, and operation of the device, along with the information required to reproduce and validate its performance.

### 1.2 Safety

- Do not expose the interior of the device to water
- Unplug the device when not in use
- Do not leave the device unattended while operating
- Keep hands and other objects away from the spinning motor and attachments while in operation.

## 2 Package Contents

All of the components required to make the device are listed in the tables below. The tables are broken up into the individual sub-assemblies that make up the device.

### Attachment Storage

Part Name | Quantity | Supplier | Part Number / Description
Foam Panel | 1 | Custom | Foam Divider
Front Panel | 1 | Custom | Front Panel of the lid
Rear Lid Panel | 1 | Custom | Back Panel of the lid
6 1/2 Thread Forming Screw | 4 | McMaster Carr | 90385A148

### Box Internal Structure

Part Name | Quantity | Supplier | Part Number / Description
Plate Bend Inlet | 1 | Custom | Top Panel of the box interior
Housing | 1 | Custom | Trough for motor housing
Arduino Uno | 1 | Arduino Store | Arduino Uno R3
PCB | 1 | Custom | Circuit board that connects all electrical components
Motor Controller | 1 | Adafruit | DRV8871
Power Port | 1 | Digikey | Switchcraft 712AFMS
USB Port | 1 | Digikey | Cliff CP30608NX1
6-32 1/2 Machine Screw | 6 | McMaster-Carr | 90279A148
6-32 Locknut | 6 | McMaste-rCarr | 90631A007
4-40 1/2 Machine Screw | 2 | McMaster-Carr | 90279A110
4-40 Nut | 2 | McMaster-Carr | 91841A005
PCB Mounting Plate | 1 | Custom | Acrylic Mounting Plate for PCB
6 1/2 Thread Forming Screw | 5 | McMaster-Carr | 90385A148
Nanuk 905 Case | 1 | Nanuk | Case the device is built in
Cable Gromet | 1 | Digikey | Essentra Components DG-
| | | 10134
Power Source | 1 | Digikey | Mean Well GST90A24-P1M
USB A to USB B | 1 | Amazon | Belkin F3U133-06INCH
Encoder Cord | 1 | US Digital | CA-MIC4-W4-NC

### Attachments

Part Name | Quantity | Supplier | Part Number / Description
Intertia Disk | 1 | Custom | Aluminum disk
Neodinium Magnets | 8 | Tinycircuits | 6 mm X 4 mm
Pendulum Housing | 1 | Custom | Cylindrical Component of the Pendulum
Encoder | 1 | US Digital | E8T
M2.5x0.45 Screw | 2 | McMaster-Carr | 92000A105
Bearings | 2 | McMaster-Carr | 57155K323
8-32 Socket Head Screw | 1 | McMaster-Carr | 91274A048
Pendulum Shaft | 1 | Custom | N/A

1/4 in Retaining Ring | 2 | McMaster-Carr | 98410A113
4-40 1/8 in Set Screw | 1 | McMaster-Carr | 94355A130
Pendulum Arm | 1 | Custom | N/A
Aux Cord | 1 | Amazon | 3.5mm Male Plug to 4Pin Bare Wire
Encoder Cord | 1 | US Digital | CA-MIC4-W4-NC

### Motor Housing

Part Name | Quantity | Supplier | Part Number / Description
Motor Plate | 1 | Custom | Top Plate of Motor Housing
Motor Legs | 2 | Custom | Sidewalls of Motor Housing
Motor | 1 | Maxon | DC-max 26 S Ø26 mm, CLL pre- cious metal brushes, sintered bearings
Encoder | 1 | US Digital | E8T
Adhesive | 1 | Amazon | 3M 300lse
Aux Port | 1 | Digikey | Same Sky SJ1-43502PM
Pendulum Stop | 1 | Custom | 3D printed part that protects the pendulum AUX cord
6-32 1/2 Machine | 4 | McMaster-Carr | 90279A148
6-32 Locknut | 4 | McMaster-Carr | 90631A007
4-40 1/2 Machine Screw | 2 | McMaster-Carr | 90279A110
4-40 Nut | 2 | McMaster-Carr | 91841A005
M2 8 machine Screw | 2 | McMaster-Carr | 92005A029
Attachment Interface | 1 | Custom | Connects device attachments to the motor
2-56 3/16 Set Screw | 1 | McMaster-Carr | 92311A076
10-32 1-1/4 Partially Threaded Socket Head | 2 | McMaster-Carr | 90128A948
Nylon Washer | 4 | McMaster-Carr | 90295a639
10-32 Nut | 4 | McMaster-Carr | 91841A195
Neodinium Magnets | 4 | Tinycircuits | 6 mm X 4 mm

## 3 Materials/Tools Required

### 3.1 Hardware

- Computer capable of running the software in Section 3.2
- Soldering Iron
- Pendulum encoder wires, motor wires, and motor encoder wires
- Heat Shrink

- Crescent Wrenches
- Philips Screwdrivers
- Allen Wrenches

### 3.2 Software

- MATLAB (Windows or Linux Versions)
- Simulink (Windows or Linux Versions)
- Arduino IDE (Windows or Linux Versions)
- All software downloaded from the “C.E.W.B” GitHub Software section

## 4 Procedure

### 4.1 Assembly

4.1.1 Pendulum Subassembly

The pendulum assembly seats onto the interface on the motor via a magnetic connection. Primary parts are the pendulum mount, arm, and shaft joined with two bearings, retaining rings, and a cap screw for the arm.

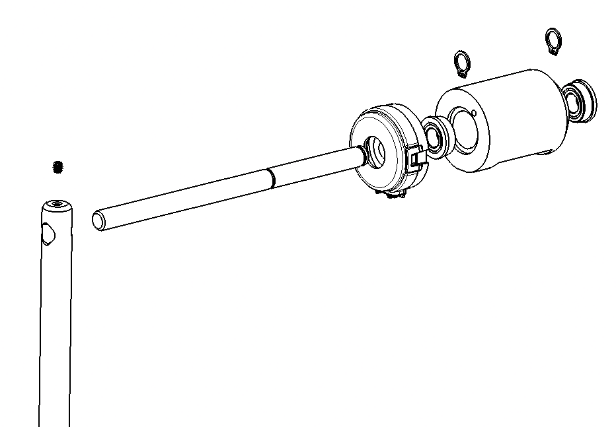
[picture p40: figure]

1) Press-fit bearings into either side of the pendulum mount
2) Insert the pendulum shaft through both bearings in the pendulum mount
3) Place one retaining on the end-groove of the shaft by the butt of the mount
4) Place the second ring on the second groove near the face of the mount
5) Apply the encoder assembly over the pendulum shaft against the flat face of the mount
6) Insert the shaft of the assembly through the hole in the pendulum arm and secure the connection with a set screw leaving 0.25 inch
of the shaft beyond the arm

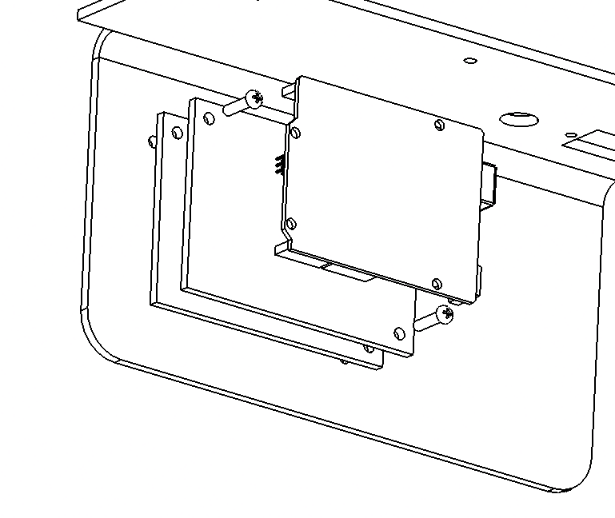
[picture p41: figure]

4.1.1 Internal Hardware Subassembly

1) Stack the PCB onto the acrylic mounting plate
2) Insert two screws into opposite corners of the plates and through the primary bent plate
3) Secure equally sized screws to the ends of each screw
4) Apply the Arduino to the PCB in the orientation shown

4.1.1 Hinge Subassembly

1) Insert the partially threaded socket head screw through the outside of the side of the trough
2) Apply a nylon washer to the screw against the inner face of the trough
3) Put one of the legs onto the screw with the bend pointing inward
4) Apply another nylon washer followed by
two nuts to the screw

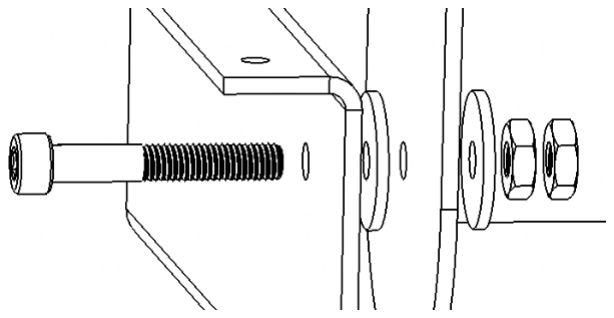
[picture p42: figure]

5) Torque the inner nut to allow movement but allow the assembly to remain upright. Apply the second nut to secure the joint. It should allow free pivot of the joint, but will remain in one place and not fall into the trough
6) Repeat for the second leg

4.1.1 Motor Plate Subassembly

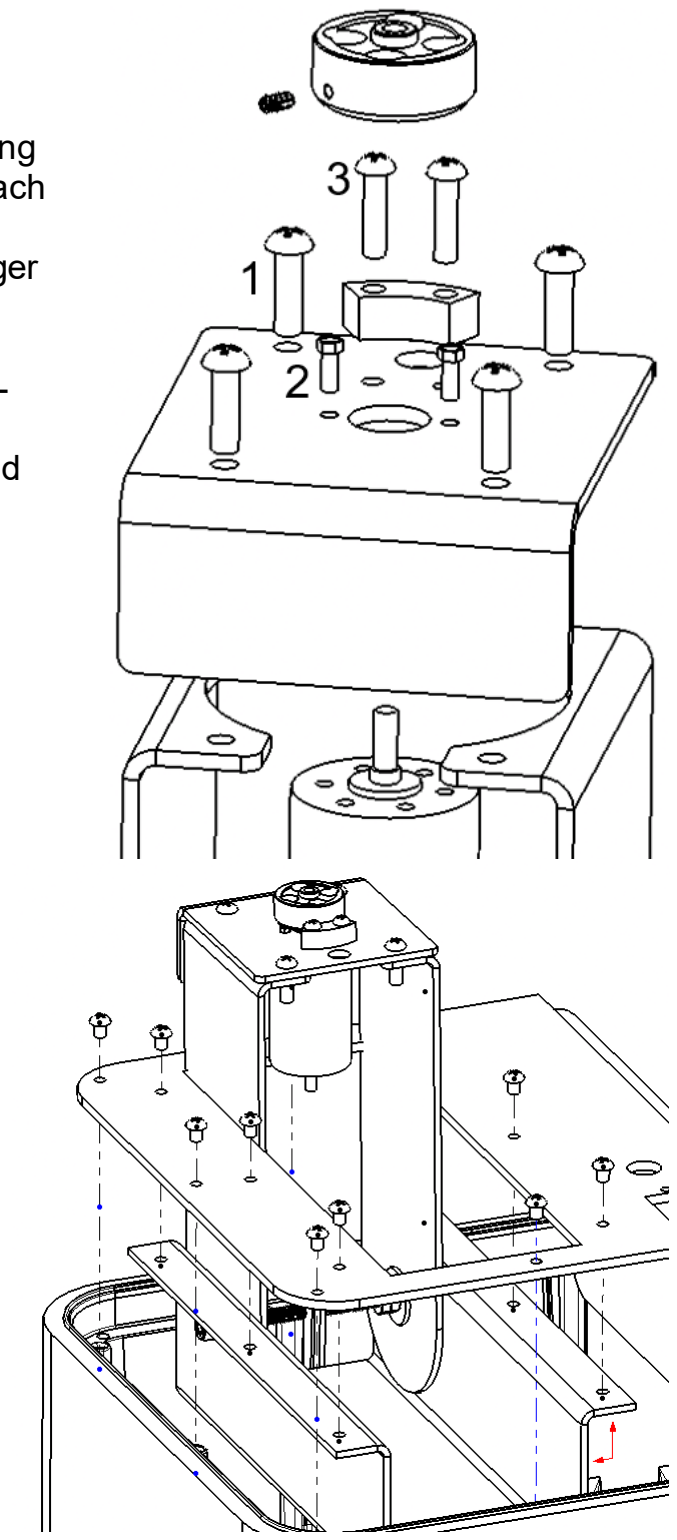
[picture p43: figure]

1) Secure the bent face plate to the top of the legs using the #6 screws labeled (1) in the diagram. Secure each with a #6 nut
2) Insert the motor through the face plate with the longer motor shaft upward. Secure the motor with two M2 screws labeled (2)
3) Secure the plastic stop-piece with two #4 screws labeled (3) and #4 nuts on each screw
4) Fit the attachment interface onto the motor shaft and secure it with a set screw

4.1.1

1) Place the main bent baseplate over the pendulum mount, onto the trough as shown
2) Secure six #6 screws with appropriate lock nuts
3) Secure a rubber gromet into the hole at the bottom of the trough
4) (Not Pictured) Thread all wires from Arduino through hole in bottom of trough
5) With wiring connections secured, place the full assembly into bottom of case
6) Secure into place with 5 thread-forming screws

4.1.1

1) Press-fit magnets into the 8 small holes in the smaller board – Apply glue to the inner surface for each magnet individually
2) Glue the laser cut foam panel to the smaller, rear board Orient the large rectangular
cut on the right, with the cut
for the pendulum on top

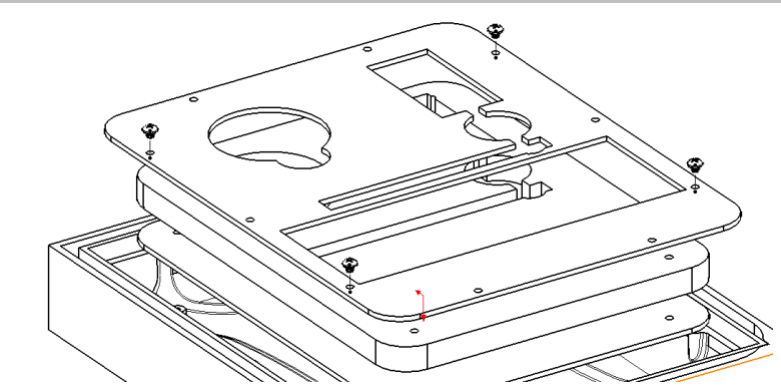
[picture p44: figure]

3) Glue the other side of the foam to the back of the larger board, aligning the cuts
4) After glue has cured, use thread-forming screws to secure the assembly into place

### 1.2 Operation

NOTE: BEFORE USE, MAKE SURE THE MOTOR HOUSING IS IN THE UPRIGHT POSITION AND THE POWER AND COMPUTER CABLES, ALONG WITH ANY OTHER OBJECTS, ARE AWAY FROM THE MOTOR SHAFT!

1. Create and open a blank Simulink file. This file must be created in the same folder/location as the “ArduinoSerial.m” MATLAB file for the system to work.

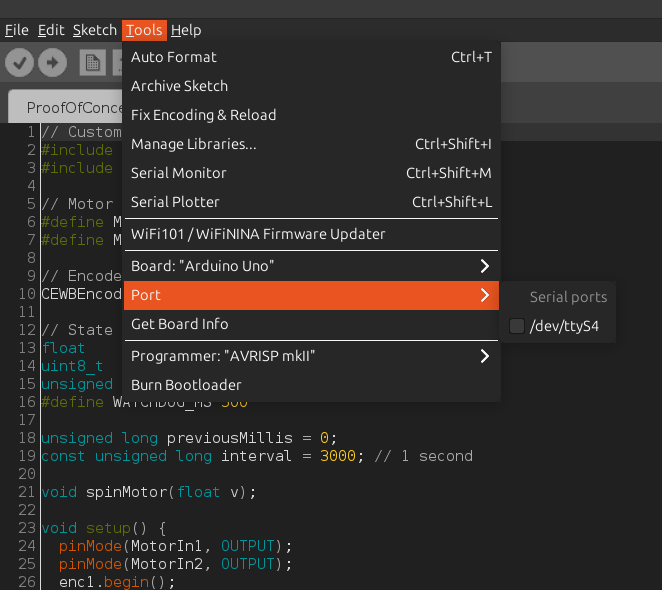
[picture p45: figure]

2. In the “ArduinoSerial.m” file, in the COMSPORT line, the port that the Arduino is connected to needs to be listed there. To check the exact name of the port, connect the Arduino to the user’s PC and open Arduino IDE. Go to Tools, then go to the Ports option. The connected port that is listed with the Arduino Uno is the port needed. Copy the port name and add it to the COMSPORT line in the “ArduinoSerial.m” file.

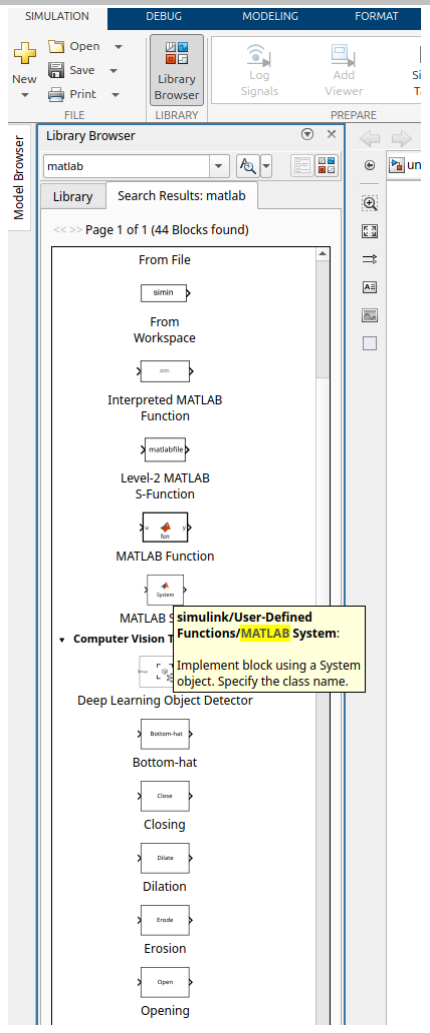
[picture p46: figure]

3. While in Simulink, navigate to the Library Browser menu, find the MATLAB System block, and drag it onto the Simulink work area.

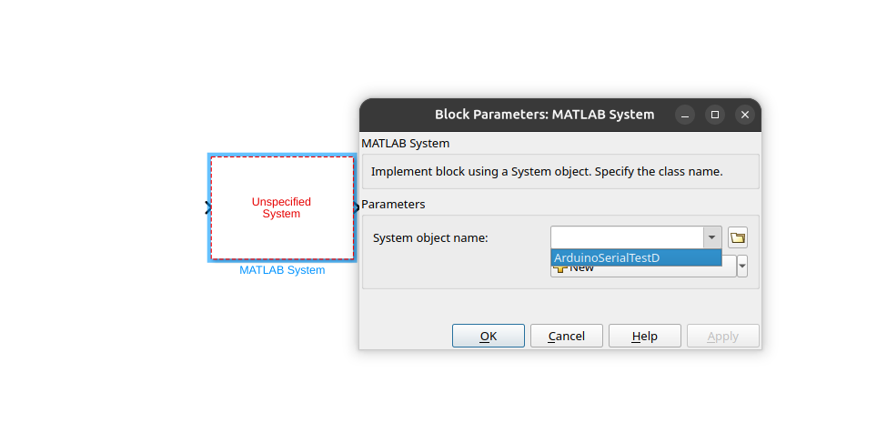
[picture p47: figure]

4. The MATLAB System block will be red and unusable at first. Click on the block, then in the dropdown click on the “ArduinoSerial” option and “OK”.

### 5. NOTE: IF THE “ARDUINOSERIAL” OPTION DOES NOT APPEAR, THAT MATLAB FILE

EITHER IS NOT IN THE SAME FOLDER AS THE SIMULINK MODEL. GO BACK AND MAKE SURE IT IS THERE!

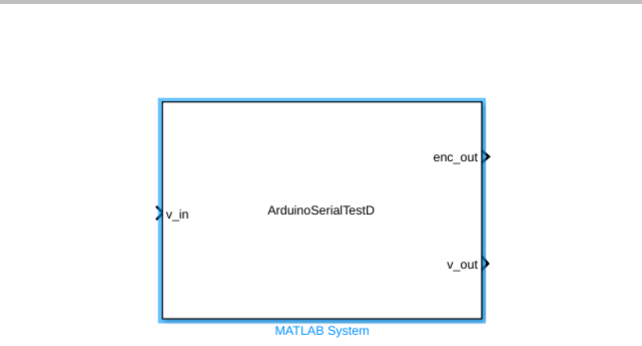
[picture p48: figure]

6. When the “ArduinoSerial” is selected, the MATLAB System will transform into a block labelled "ArduinoSerial” and have one input labeled “v_in” and two outputs labeled “enc_out” and “v_out”.

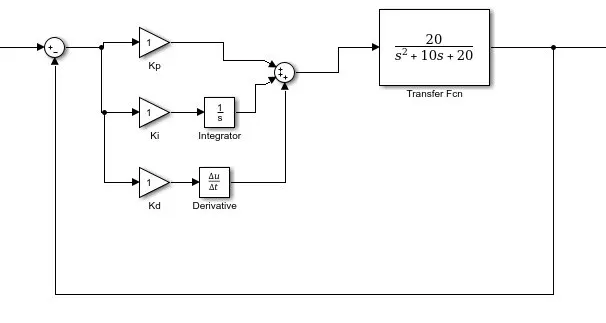
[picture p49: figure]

7. Once the setup is complete, the “enc_out” value can be used for the PID controller. The output of the “enc_out” is position count, so a calculation of 360 deg or 2*pi rads divided by 2048 can be used to find the angle of the system, while the derivative can be but in to find the speed of the system.

### 1.3 Maintenance

### 1.4 Storage

The steps below describe how the device should be broken down for storage when not in use.

1. Unplug the USB cable from your computer and from the device, and the power cable from the device and the wall.
2. Unplug the power cable from the power supply brick and place the brick into the storage compartment on the left side of the device. Coil the power cable and place it into the storage compartment on top of the brick. Place the USB cable in the storage compartment and ensure that all of the cables are under the panel and will allow the lid to close.
3. Remove all attachments that were used and place them in their respective storage locations in the lid.

4. Fold the motor housing down in the trough, being careful to ensure that wires are not catching on anything.
5. Close the lid and lock the two latches on the side.

## 2 Troubleshooting

The table below provides information on how to solve common problems that might arise during use of the device. Find the problem you are experiencing under the issues column and determine the proper fix under the corrective action column.

Issue | Cause(s) | Corrective Action
Loose Motor Housing | Hinge loosening | Tighten hinge bolt and nuts
Motor Not Working | Loose/Missing Connection(s)
| Motor Driver Fault

Run the “MotorRamp-SpeedTest.ino” script in the “ArduinoTests” folder in “ExamplesAndTests”. If it doesn’t work, then open the CEWB and test connections for and make sure the CEWB is plugged in. If still not working, test/replace the motor driver

Encoder Not Working | Loose/Missing Connection(s)

Run the “Encoder-QuadTest.ino” script in the “ArduinoTests” folder in “ExamplesAndTests”. If it still doesn’t work, then open the encoder and ensure that it is still optical piece is on and in the right place.

## 3 Technical Support

For questions regarding the motor, contact maxon motors at info.us@maxongroup.com or
call (508) 677-0520.

For questions regarding the optical encoders, contact US Digital at support@usdigital.com or call 800-736-0194.

The 3D models for all of the custom components can be found on the GitHub Repository by following this link

https://github.com/aJax-EXE/C.E.W.B./tree/main/Hardware/3DModels/CurrentVersion

For any other questions regarding the device, contact Dr. Talles Santos by email at Talles.Santos@colorado.edu

## 4 Spare Parts/Components

A list of all of the parts making up the device, as well as part numbers and supplier information, are listed under the package contents section.

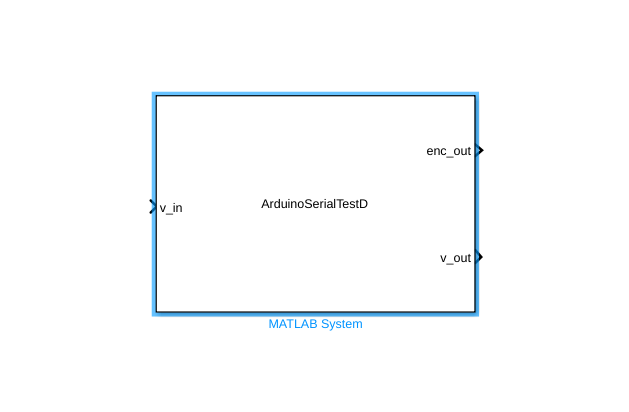
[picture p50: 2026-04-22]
Images/InstructionImages/CorrectMatlabSystemBlock.png

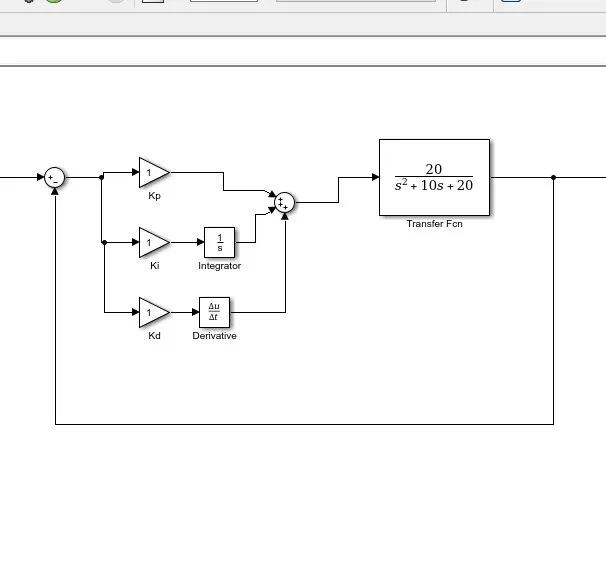
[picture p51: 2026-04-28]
Images/InstructionImages/ExamplePIDControllerBlockDiagram.webp

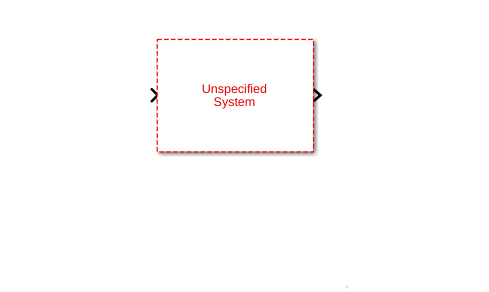
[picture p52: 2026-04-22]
Images/InstructionImages/Screenshot From 2026-04-22 10-26-20.png

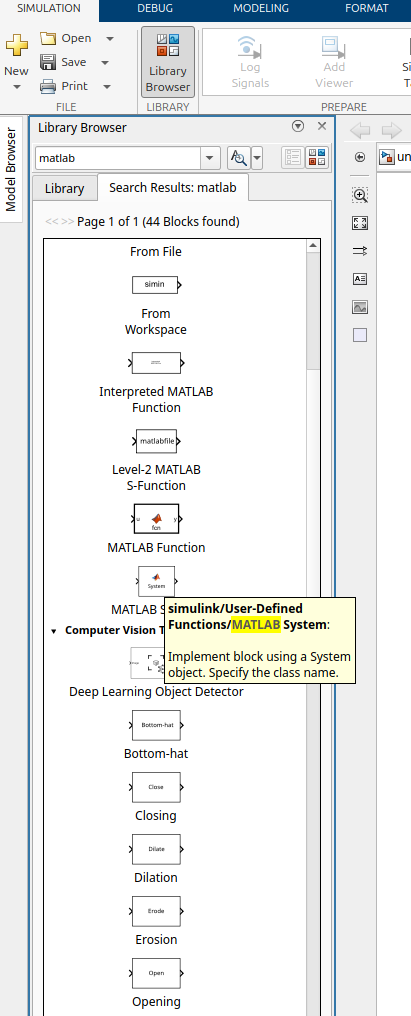
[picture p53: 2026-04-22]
Images/InstructionImages/SimulinkLibraryMatlabOption.png

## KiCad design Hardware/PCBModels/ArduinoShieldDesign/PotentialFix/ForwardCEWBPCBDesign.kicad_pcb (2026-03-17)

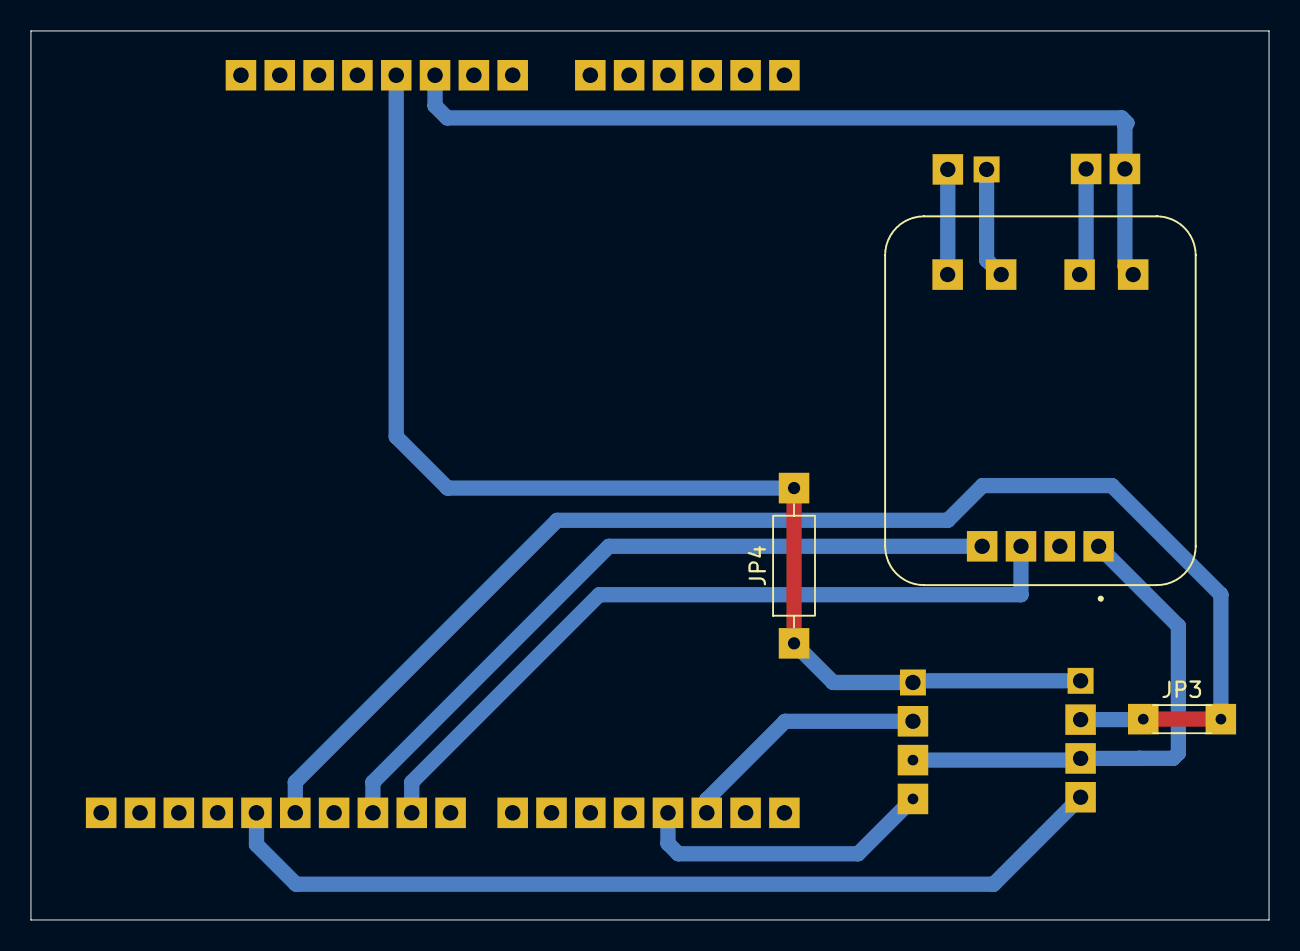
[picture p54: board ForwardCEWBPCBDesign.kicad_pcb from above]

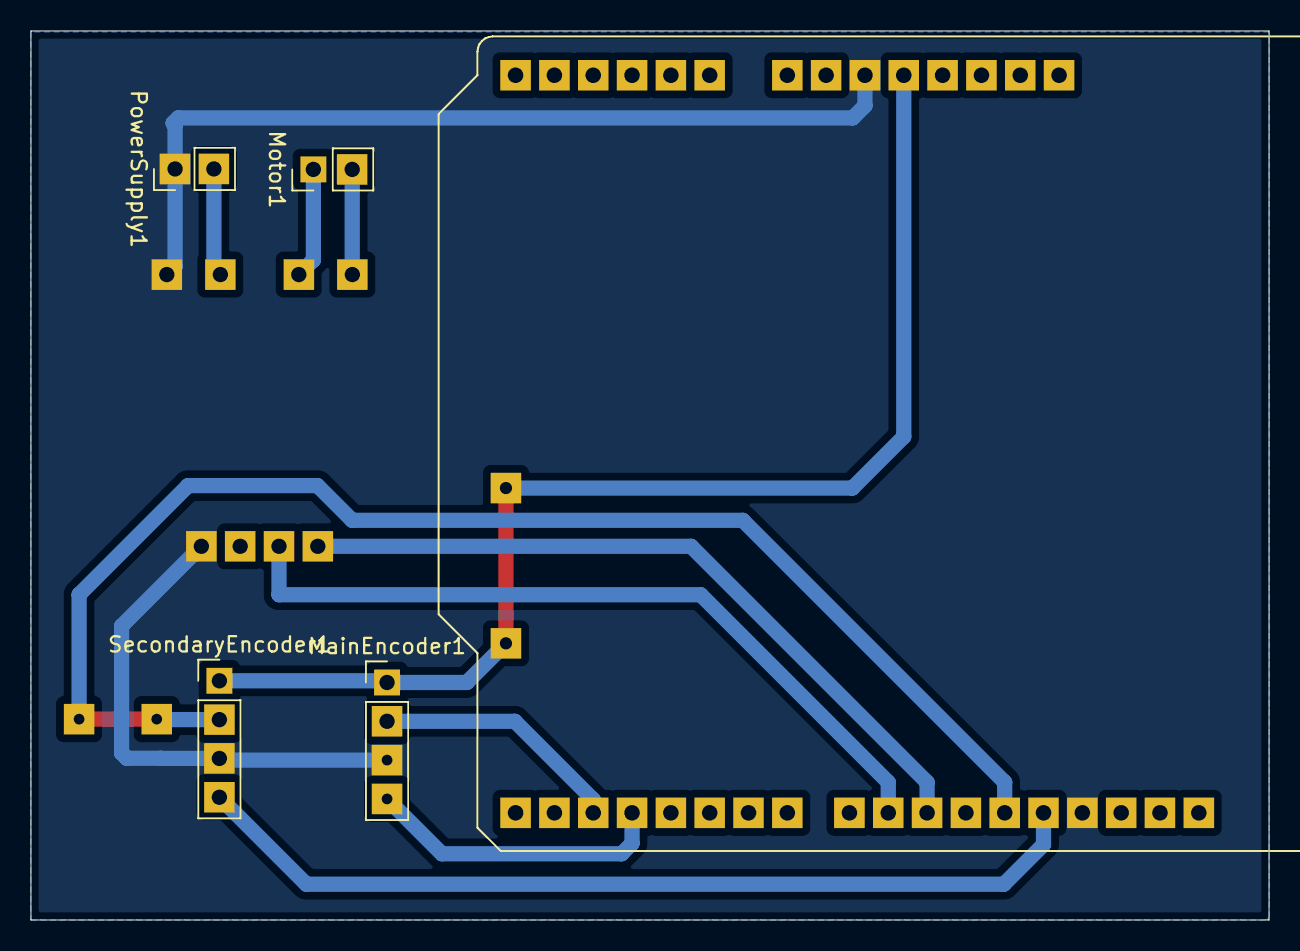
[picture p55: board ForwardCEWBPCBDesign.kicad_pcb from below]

Board: 2 copper layers, 81.0 x 58.2 mm, 8 parts (5 on the bottom side), 11 nets.

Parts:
A1: A000066; ARDUINO_A000066
DRV1: DRV8871_manual
JP3: Jumper_2_Bridged; R_Axial_DIN0204_L3.6mm_D1.6mm_P5.08mm_Horizontal
JP4: Jumper_2_Bridged; R_Axial_DIN0207_L6.3mm_D2.5mm_P10.16mm_Horizontal
MainEncoder1: Conn_01x04_Pin; PinHeader_1x04_P2.54mm_Vertical
Motor1: Conn_01x02_Pin; PinHeader_1x02_P2.54mm_Vertical
PowerSupply1: Conn_01x02_Pin; PinHeader_1x02_P2.54mm_Vertical
SecondaryEncoder1: Conn_01x04_Pin; PinHeader_1x04_P2.54mm_Vertical

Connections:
+5C: A1.5V, JP4.1 (A), JP4.2 (B), MainEncoder1.1, SecondaryEncoder1.1
/D12: A1.D12, JP3.1 (A), JP3.2 (B), SecondaryEncoder1.2
/D13: A1.D13, SecondaryEncoder1.4
/In1: A1.D9, DRV1.2 (In1)
/In2: A1.D10, DRV1.1 (In2)
GND: A1.GND_2, A1.GND_3, DRV1.4 (GND), DRV1.5 (PW_-), MainEncoder1.3, PowerSupply1.1, SecondaryEncoder1.3
unnamed: DRV1.7 (Out_1), Motor1.1
unnamed: DRV1.8 (Out_2), Motor1.2
unnamed: DRV1.6 (PW_+), PowerSupply1.2
unnamed: A1.D2, MainEncoder1.2
unnamed: A1.D3, MainEncoder1.4

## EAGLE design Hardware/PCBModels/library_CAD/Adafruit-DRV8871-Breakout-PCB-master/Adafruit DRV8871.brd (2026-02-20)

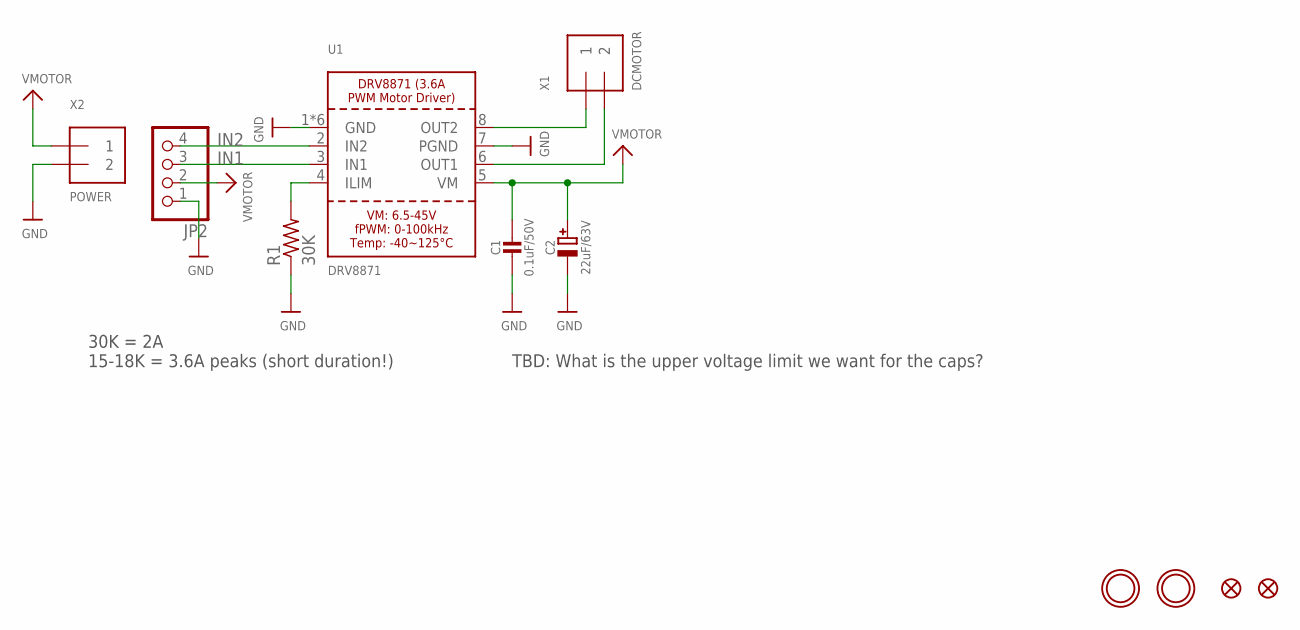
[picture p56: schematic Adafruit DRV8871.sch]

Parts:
C1: 0.1uF/50V; 0805-NO
C2: 22uF/63V; PANASONIC_D
FID1, FID2: FIDUCIAL""; FIDUCIAL_1MM
JP2: HEADER-1X476MIL; 1X04_ROUND_76
R1: 30K; 0805-THM
U1: DRV8871; HSOP8
U$9, U$10: MOUNTINGHOLE2.5; MOUNTINGHOLE_2.5_PLATED
X1: DCMOTOR; TERMBLOCK_1X2-3.5MM
X2: POWER; TERMBLOCK_1X2-3.5MM

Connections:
GND: C1.2, C2.-, JP2.1, R1.1, U1.1 (GND), U1.7 (PGND), U1.GND, U1.P$1 (GND), U1.P$2 (GND), U1.P$3 (GND), U1.P$4 (GND), X2.2
IN1: JP2.3, U1.3 (IN1)
IN2: JP2.4, U1.2 (IN2)
unnamed: R1.2, U1.4 (ILIM)
OUT1: U1.6 (OUT1), X1.2
OUT2: U1.8 (OUT2), X1.1
VMOTOR: C1.1, C2.+, JP2.2, U1.5 (VM), X2.1

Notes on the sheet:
TBD: What is the upper voltage limit we want for the caps?
30K = 2A 15-18K = 3.6A peaks (short duration!)

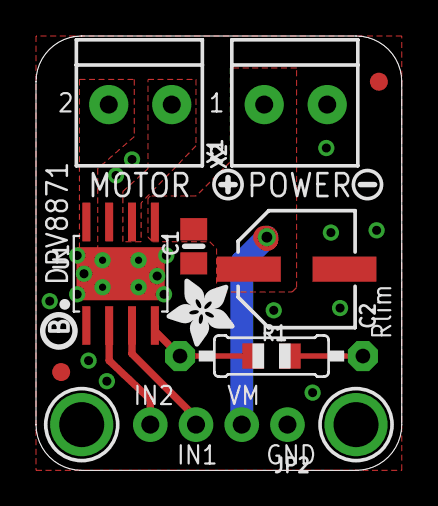
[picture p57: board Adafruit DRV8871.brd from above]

Board: 2 copper layers, 20.3 x 24.1 mm, 15 parts (0 on the bottom side), 7 nets.

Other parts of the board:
U$11: SYMBOL_PLUS
U$12: SYMBOL_MINUS
U$14: ADAFRUIT_3.5MM
U$15: PCBFEAT-REV-040

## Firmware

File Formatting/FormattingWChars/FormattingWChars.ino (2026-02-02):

// Setting the variables that the format will carry (Change the values to see the results)
// USES CHAR ARRAYS

// Struct of the different type of variables that will be given the information from the char array
struct parsedData {
  // The first value should indicate if the info is the Master/Setting form '$' or the Feedback form '#'
  char infoType = '$';

  // Voltage should have the form XX.XXXX
  float voltage = 12.3220;

  // The angle type either be a 'D' for degrees or 'R' for radians
  char angleType = 'D';

  // Angle, regardless of the type, should have the form XXX.XXXX
  float angle = 44.8745;

  // The Kp, Ki, and Kd values should have the form XXX.XXXX
  float Kp = 9;
  float Ki = 0.1;
  float Kd = 3.5;

  // Array that will hold an error message to tell the user what is wrong
  // Will deal with the error code messages
  char errMsg[100];
};

// Creating the struct
parsedData results;

// The size of the char array buffer for which will tell how big the formatted info will be
const int bufferSize = 50;

// The end character is '!', which signals the end of the information
// The complete information format that needs to be dissected (and the temp info variable)
char info[bufferSize] = " ";

// Check if all of the values are formatted correctly or can be formatted correctly
bool correctFormat, done = false;

// Binary counter to determine what values are incorrect and need to be fixed 
// (And with the different types of error values that can exist)
uint8_t errorVal = 0b000000;
enum Errors {
  INFO_TYPE_ERROR  = 0b100000,
  VOLT_ERROR       = 0b010000,
  ANGLE_TYPE_ERROR = 0b001000,
  KP_ERROR         = 0b000100,
  KI_ERROR         = 0b000010,
  KD_ERROR         = 0b000001
};

// Functions used for the formatting
bool formatCheck(char, float, char, float, float, float, float, byte&);
void transferValues(char, float, char, float, float, float, float, char*, int);
void failState();

void setup() {
  // put your setup code here, to run once:
  Serial.begin(9600);
  Serial.println("=================================");
}

void loop() {
  // 'done' variable makes sure the code only runs once
  while (!done) {
    // Checking the formatting and values of the input values to be compared
    correctFormat = formatCheck(results.infoType, results.voltage, 
                                results.angleType, results.Kp, results.Ki, 
                                results.Kd, errorVal);
    
    if (!correctFormat) {
      // Checks failed somewhere...
      Serial.println("Sorry user, but one or more of the following variables 
                      inputted for proper formatting are incorrect: ");

      // Check each bit and print corresponding message
      if (errorVal & INFO_TYPE_ERROR) {
        Serial.println("* Incorrect information type character given");
      }
      if (errorVal & VOLT_ERROR) {
        Serial.println("* Incompatiable voltage value given");
      }
      if (errorVal & ANGLE_TYPE_ERROR) {
        Serial.println("* Incorrect angle type given");
      }
      if (errorVal & KP_ERROR) {
        Serial.println("* Incompatiable Kp value given");
      }
      if (errorVal & KI_ERROR) {
        Serial.println("* Incompatiable Ki value given");
      }
      if (errorVal & KD_ERROR) {
        Serial.println("* Incompatiable Kd value given");
      }
      
      Serial.println("Please review and try again.");
      done = true;
    } else {
        // Check succeeds
        transferValues(results.infoType, results.voltage, results.angleType, 
                       results.angle, results.Kp, results.Ki, results.Kd, 
                       info, bufferSize);

        // The overall length of the formatted information array should be 49 characters long (48 info characters + '\0' (null character))
        Serial.print("Formatted Info: ");
        Serial.println(info);
        Serial.print("Number of info characters: ");
        Serial.println(strlen(info));
        Serial.print("Number of total characters: ");
        Serial.println(strlen(info) + 1);
        done = true;
    }
  }
}

// Function that checks if the given values are valid and can be formatted correctly
bool formatCheck(char infoType, float voltage, char angleType, float Kp, 
                 float Ki, float Kd, byte& error) {
  if (infoType != '$' && infoType != '#') {
    error |= INFO_TYPE_ERROR;
  }
  if (voltage/100 >= 1) { 
    error |= VOLT_ERROR;
  }
  if (angleType != 'D' && angleType != 'R') {
    error |= ANGLE_TYPE_ERROR;
  }
  if (Kp/1000 >= 1 || Ki/1000 >= 1 || Kd/1000 >= 1){
    if (Kp/1000 >= 1) {
      error |= KP_ERROR;
    } 
    if (Ki/1000 >= 1) {
      error |= KI_ERROR;
    }
    if (Kd/1000 >= 1) {
      error |= KD_ERROR;
    }
  }

  return error == 0;
}

// Function that turns the float values into there proper form of XXX.XXXX into a char array
void transferValues(char infoType, float voltage, char angleType, float angle, 
                    float Kp, float Ki, float Kd, char* info, int bufferSize) {
  // Variables for the whole number and decimal points of each value
  int wholeVolt = (int)voltage;
  int wholeAng = (int)angle;
  int wholeKp = (int)Kp;
  int wholeKi = (int)Ki;
  int wholeKd = (int)Kd;

  int fracVolt  = round((voltage - wholeVolt) * 10000);
  int fracAng  = round((angle - wholeAng) * 10000);
  int fracKp  = round((Kp - wholeKp) * 10000);
  int fracKi  = round((Ki - wholeKi) * 10000);
  int fracKd  = round((Kd - wholeKd) * 10000);

  // Combining all of the variables together into the necessary format
  snprintf(info, bufferSize, "%cV%02d.%04dA%c%03d.%04d;P%03d.%04dI%03d.%04dD%03d.%04d!", 
           infoType, wholeVolt, fracVolt, angleType, wholeAng, fracAng, wholeKp, fracKp, 
           wholeKi, fracKi, wholeKd, fracKd);
} 

void failState() {
  // Check failed somewhere...
  results.infoType = 'N';
  results.voltage = 0;
  results.angleType = 'N';
  results.angle = 0;
  results.Kp = 0;
  results.Ki = 0;
  results.Kd = 0;

  Serial.print("Check val: ");
  Serial.println(charCheck);
  Serial.print("incorrect val: ");
  Serial.println(incorrectChar);
  Serial.print("short val: ");
  Serial.println(tooShort);
  // Outputting the correct reason of error message
  if (charCheck & incorrectChar) {
    Serial.println(charCheck);
    strcpy(results.errMsg, "Characters in the wrong order");
  } else if (charCheck & tooShort) {
    Serial.println(charCheck);
    strcpy(results.errMsg, "Info too short");
  }
}

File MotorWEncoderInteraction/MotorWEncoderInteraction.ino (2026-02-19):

// ================= CONFIG =================
#define ENC_A 2
#define ENC_B 3

#define IN1 9   // PWM pin
#define IN2 8

// encoder resolution AFTER quadrature
// example: 600 CPR encoder → 2400 counts
const float COUNTS_PER_REV = 2400.0;

// PID gains (tune these!)
float Kp = 4.0;
float Ki = 0.02;
float Kd = 0.2;

// ================= GLOBALS =================

volatile long encoderCount = 0;

float targetAngle = 90.0;   // degrees (change this!)

float integral = 0;
float lastError = 0;

unsigned long lastTime;

// ================= ENCODER ISR =================

void encoderISR() {
  bool A = digitalRead(ENC_A);
  bool B = digitalRead(ENC_B);

  if (A == B) encoderCount++;
  else encoderCount--;
}

// ================= SETUP =================

void setup() {
  Serial.begin(115200);

  pinMode(ENC_A, INPUT_PULLUP);
  pinMode(ENC_B, INPUT_PULLUP);

  pinMode(IN1, OUTPUT);
  pinMode(IN2, OUTPUT);

  attachInterrupt(digitalPinToInterrupt(ENC_A), encoderISR, CHANGE);
  attachInterrupt(digitalPinToInterrupt(ENC_B), encoderISR, CHANGE);

  lastTime = millis();
}

// ================= MOTOR DRIVER =================

void setMotor(float value) {

  value = constrain(value, -255, 255);

  if (value > 0) {
    // Forward
    analogWrite(IN1, value);
    digitalWrite(IN2, LOW);
  }
  else if (value < 0) {
    // Reverse
    analogWrite(IN1, -value);
    digitalWrite(IN2, HIGH);
  }
  else {
    // Brake / coast
    digitalWrite(IN1, LOW);
    digitalWrite(IN2, LOW);
  }
}


// ================= MAIN LOOP =================

void loop() {

  // ----- Time step -----
  unsigned long now = millis();
  float dt = (now - lastTime) / 1000.0;
  lastTime = now;

  // ----- Get angle -----
  noInterrupts();
  long counts = encoderCount;
  interrupts();

  float angle = counts * 360.0 / COUNTS_PER_REV;

  // ----- PID -----
  float error = targetAngle - angle;

  integral += error * dt;
  integral = constrain(integral, -100, 100);   // anti-windup

  float derivative = (error - lastError) / dt;
  lastError = error;

  float output = Kp * error + Ki * integral + Kd * derivative;

  // ----- Drive motor -----
  setMotor(output);

  // ----- Debug -----
  Serial.print("Angle: ");
  Serial.print(angle);
  Serial.print("  Output: ");
  Serial.println(output);

  delay(5);
}

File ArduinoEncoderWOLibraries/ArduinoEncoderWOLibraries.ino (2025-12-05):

// Rotary Encoder Inputs
#define CLK 6 // White Wire
#define DT 5  // Green Wire

// Motor Drive PMW Pins
#define MotorIn1 9  // Orange Wire
#define MotorIn2 10 // Blue Wire

int counter = 0;
int currentStateCLK;
int lastStateCLK;
String currentDir = "";

int PWMVal = 0;

void setup() {

  // Set encoder pins as inputs
  pinMode(CLK, INPUT);
  pinMode(DT, INPUT);

  // Setting the Motor Pins
  pinMode(MotorIn1, OUTPUT);
  pinMode(MotorIn2, OUTPUT);

  // Setup Serial Monitor
  Serial.begin(9600);

  // Read the initial state of CLK
  lastStateCLK = digitalRead(CLK);
}

void loop() {

  // Read the current state of CLK
  currentStateCLK = digitalRead(CLK);

  // Ramp Up Forward
  digitalWrite(MotorIn1, LOW);
  for (PWMVal; PWMVal <= 100; PWMVal++) {
    currentStateCLK = digitalRead(CLK);
    analogWrite(MotorIn2, PWMVal);
    // positionCheck();
    delay(10);
  }

  // Full Forward Speed for one second
  // Figure out how to pause the process for this time while keeping 
  // The counter from the encoder going
  delay(1000);

  // Ramp Down Forward
  for (PWMVal; PWMVal >= 0; PWMVal--) {
    currentStateCLK = digitalRead(CLK);
    analogWrite(MotorIn2, PWMVal);
    // positionCheck();
    delay(10);
  }

  // Ramp Up Backward
  digitalWrite(MotorIn2, LOW);
  for (PWMVal = 0; PWMVal <= 100; PWMVal++) {
    currentStateCLK = digitalRead(CLK);
    analogWrite(MotorIn1, PWMVal);
    // positionCheck();
    delay(10);
  }

  // Full Backwards Speed for one second
  // Figure out how to pause the process for this time while keeping 
  // The counter from the encoder going
  delay(1000);

  // Ramp Down Forward
  for (PWMVal = 100; PWMVal >= 0; PWMVal--) {
    currentStateCLK = digitalRead(CLK);
    analogWrite(MotorIn1, PWMVal);
    // positionCheck();
    delay(10);
  }
}

  // If last and current state of CLK are different, then pulse occurred
  // React to only 1 state change to avoid double count
//   if (currentStateCLK != lastStateCLK && currentStateCLK == 1) {

//     // If the DT state is different than the CLK state then
//     // the encoder is rotating CCW so decrement
//     if (digitalRead(DT) != currentStateCLK) {
//       counter--;
//       currentDir = "CCW";
//     } else {
//       // Encoder is rotating CW so increment
//       counter++;
//       currentDir = "CW";
//     }

//     Serial.print("Direction: ");
//     Serial.print(currentDir);
//     Serial.print(" | Counter: ");
//     Serial.println(counter);
//   } else {
//     Serial.print("Direction: ");
//     Serial.print(currentDir);
//     Serial.print(" | Counter: ");
//     Serial.println(counter);
//   }

//   // Remember last CLK state
//   lastStateCLK = currentStateCLK;
//   // counter++;

// }

// void positionCheck () {
//   // If last and current state of CLK are different, then pulse occurred
//   // React to only 1 state change to avoid double count
//   if (currentStateCLK != lastStateCLK && currentStateCLK == 1) {

//     // If the DT state is different than the CLK state then
//     // the encoder is rotating CCW so decrement
//     if (digitalRead(DT) != currentStateCLK) {
//       counter--;
//       currentDir = "CCW";
//     } else {
//       // Encoder is rotating CW so increment
//       counter++;
//       currentDir = "CW";
//     }

//     Serial.print("Direction: ");
//     Serial.print(currentDir);
//     Serial.print(" | Counter: ");
//     Serial.println(counter);
//   } //else {
//   //   Serial.print("Direction: ");
//   //   Serial.print(currentDir);
//   //   Serial.print(" | Counter: ");
//   //   Serial.println(counter);
//   // }

//   // Remember last CLK state
//   lastStateCLK = currentStateCLK;
// }

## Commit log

2025-09-15 Arduino Encoder Works, but acts funny?
2025-11-03 Arduino to C++ Test Begin
2025-11-10 current progress
2025-11-13 More Testing Writing from Txt to Arduino Start
2025-11-17 Syncing Current Progress to Github
2025-12-01 Added the Circuit Diagram
    [C.E.W.B. Circuit Diagram.fzz]
2025-12-05 Some cleaning
    [C.E.W.B. Circuit Diagram.fzz]
2026-01-06 Current progress up to date
2026-02-06 Taking data from the arduino and putting it to the terminal and text file
2026-02-20 Centralizing the Software stuff and Starting the PCB Design
    [Adafruit DRV8871.brd, Adafruit DRV8871.sch, ArduinoShieldDesign.kicad_pcb, ArduinoShieldDesign.kicad_sch]
2026-02-20 More cleaning and setting up for 3d models to be added
    [Adafruit DRV8871.brd, Adafruit DRV8871.sch, ArduinoShieldDesign.kicad_pcb, ArduinoShieldDesign.kicad_sch]
2026-02-24 KiCAD. Arduino and Driver models.
    [3190.step, Adafruit DRV8871.brd, Adafruit DRV8871.sch]
2026-02-25 Working on the PCB Design and an updated Encoder count
    [ArduinoShieldDesign.kicad_pcb, ArduinoShieldDesign.kicad_sch]
2026-02-25 PCB example.
2026-02-26 Updated PCB Design and Schematic
    [ArduinoShieldDesign.kicad_pcb, ArduinoShieldDesign.kicad_sch, CEWBPCBDesign-B_Cu.gbr, CEWBPCBDesign-Edge_Cuts.gbr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]
2026-02-26 Updated Final Gerber Files for the PCB
    [CEWBPCBDesign-B_Cu.gbr, CEWBPCBDesign-Edge_Cuts.gbr, CEWBPCBDesign-NPTH.drl, CEWBPCBDesign-PTH.drl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]
2026-03-01 Minor brd modification and Generate FlatCam files.
    [CEWBPCBDesign-B_Cu.gbr, CEWBPCBDesign-Edge_Cuts.gbr, CEWBPCBDesign-NPTH.drl, CEWBPCBDesign-PTH.drl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]
2026-03-02 Uploading the files from the 3d model
    [57155K323_Stainless Steel Ball Bearing.SLDPRT, Assun Motor.SLDPRT, Case_inner_surface.SLDPRT, Full Assembly.SLDASM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]
2026-03-04 Updated PCB Design
    [CEWBPCBDesign-B_Cu.gbr, CEWBPCBDesign-Edge_Cuts.gbr, CEWBPCBDesign-NPTH.drl, CEWBPCBDesign-PTH.drl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]
2026-03-04 New board - Generate FlatCam files.
    [CEWBPCBDesign-job.gbrjob]
2026-03-04 Final PCB Update (For Now)
    [CEWBPCBDesign-B_Cu.gbr, CEWBPCBDesign-Edge_Cuts.gbr, CEWBPCBDesign-NPTH.drl, CEWBPCBDesign-PTH.drl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]
2026-03-11 Create Past Versions
    All past 3D models of the design itterations of the device
2026-03-11 Rename Hardware/3DModels/57155K323_Stainless Steel Ball Bearing.SLDPRT to Hardware/3DModels/Prototype2/57155K323_Stainless Steel Ball Bearing.SLDPRT
    [57155K323_Stainless Steel Ball Bearing.SLDPRT]
2026-03-11 Rename Hardware/3DModels/Prototype2/57155K323_Stainless Steel Ball Bearing.SLDPRT to Hardware/3DModels/PastFiles/Prototype2/57155K323_Stainless Steel Ball Bearing.SLDPRT
    [57155K323_Stainless Steel Ball Bearing.SLDPRT]
2026-03-11 Rename Hardware/3DModels/Assun Motor.SLDPRT to Hardware/3DModels/PastFiles/Prototype2/Assun Motor.SLDPRT
    [Assun Motor.SLDPRT]
2026-03-11 Rename 57155K323_Stainless Steel Ball Bearing.SLDPRT to 57155K323_Stainless Steel Ball Bearing.SLDPRT
    [57155K323_Stainless Steel Ball Bearing.SLDPRT]
2026-03-11 Rename Assun Motor.SLDPRT to Assun Motor.SLDPRT
    [Assun Motor.SLDPRT]
2026-03-11 Rename Hardware/3DModels/Full Assembly.SLDASM to Hardware/3DModels/PastVersions/Prototype2/Full Assembly.SLDASM
    [Full Assembly.SLDASM]
2026-03-11 Rename Hardware/3DModels/Inertia Disc.SLDPRT to Hardware/3DModels/PastVersions/Prototype2/Inertia Disc.SLDPRT
    [Inertia Disc.SLDPRT]
2026-03-11 Rename Hardware/3DModels/Maxon Motor.SLDPRT to Hardware/3DModels/PastVersions/Prototype2/Maxon Motor.SLDPRT
    [Maxon Motor.SLDPRT]
2026-03-11 Rename Hardware/3DModels/Motor Arm.SLDASM to Hardware/3DModels/PastVersions/Prototype2/Motor Arm.SLDASM
    [Motor Arm.SLDASM]
2026-03-17 Basic Simulink Connection to Arduino Made and Updated PCB Models for different Arduino Board Configurations
    [CEWBPCBDesign-B_Cu.gbr, CEWBPCBDesign-Edge_Cuts.gbr, CEWBPCBDesign-NPTH.drl, CEWBPCBDesign-PTH.drl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]
2026-03-25 New milling and drilling files - Generate FlatCam files.
2026-03-26 Added the pcb for the test circuit and cleaned up some code
    [CEWBPCBDesign.kicad_pcb, CEWBPCBDesign.kicad_sch]
2026-03-30 Added a Solidworks PCB Model and Testing Simulink Connection Speed
    [ForwardCEWBPCBDesign.step]
2026-04-01 Simulink Update and pcb check
2026-04-22 Adding Images and Cleaning up
    [ForwardCEWBPCBDesign.kicad_sch]
2026-04-28 Accurate Encoder counting and trying out different solutions to the problem
    [ForwardCEWBPCBDesign.kicad_pcb, ForwardCEWBPCBDesign.kicad_sch]
2026-05-04 3D model moving
    [Motor Leg.SLDPRT, Motor Plate.SLDPRT, Pendulum Arm.SLDPRT, Pendulum Assembly.SLDASM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]

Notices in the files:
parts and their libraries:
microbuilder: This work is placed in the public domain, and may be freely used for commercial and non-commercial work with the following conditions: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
